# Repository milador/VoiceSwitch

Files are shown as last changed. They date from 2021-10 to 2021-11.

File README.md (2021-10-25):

# VoiceSwitch
An accessible voice activated switch using a HUZZAH32 – ESP32 Feather Board and an Amazon Echo

A HUZZAH32 board connected to a wheelchair using a 3.5mm audio jack (https://www.youtube.com/watch?v=OCM7eB8Ey9I)

# Setup Instructions

  Please Refer to the [Assembly Guide](https://github.com/milador/VoiceSwitch/blob/master/VoiceSwitch_Assembly_Guide.pdf).

# License 

## MIT License

Copyright (c) 2018 Milador

Permission is hereby granted, free of charge, to any person obtaining a copy of this software and associated documentation files (the "Software"), to deal in the Software without restriction, including without limitation the rights to use, copy, modify, merge, publish, distribute, sublicense, and/or sell copies of the Software, and to permit persons to whom the Software is furnished to do so, subject to the following conditions:

The above copyright notice and this permission notice shall be included in all copies or substantial portions of the Software.

THE SOFTWARE IS PROVIDED "AS IS", WITHOUT WARRANTY OF ANY KIND, EXPRESS OR IMPLIED, INCLUDING BUT NOT LIMITED TO THE WARRANTIES OF MERCHANTABILITY, FITNESS FOR A PARTICULAR PURPOSE AND NONINFRINGEMENT. IN NO EVENT SHALL THE AUTHORS OR COPYRIGHT HOLDERS BE LIABLE FOR ANY CLAIM, DAMAGES OR OTHER LIABILITY, WHETHER IN AN ACTION OF CONTRACT, TORT OR OTHERWISE, ARISING FROM, OUT OF OR IN CONNECTION WITH THE SOFTWARE OR THE USE OR OTHER DEALINGS IN THE SOFTWARE.

<p align="center">
MIT License
</p>

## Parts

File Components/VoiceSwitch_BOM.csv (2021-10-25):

Index | Quantity | Digikey Part Number | Manufacturer Part Number | Description | Unit Price (CAD) | Total Price (CAD) | Link
1 | 1 | 1528-2181-ND | 3405 | HUZZAH32 ESP32 FEATHER BOARD | 27.45 | 27.45 | https://www.digikey.ca/en/products/detail/adafruit-industries-llc/3405/7244967
2 | 1 | 1528-1658-ND | 2895 | ADAFRUIT NON-LATCHING MINI RELAY | 10.94 | 10.94 | https://www.digikey.ca/en/products/detail/adafruit-industries-llc/2895/5979891
3 | 1 | 1528-1560-ND | 2886 | FEATHER HEADER KIT FML | 1.31 | 1.31 | https://www.digikey.ca/product-detail/en/adafruit-industries-llc/2886/1528-1560-ND/
4 | 1 | 1528-1858-ND | 2750 | BATTERY LITHIUM 3.7V 350MAH (Optional) | 12.99 | 12.99 | https://elmwoodelectronics.ca/products/lithium-ion-polymer-battery-3-7v-350mah or https://www.digikey.com/en/products/detail/adafruit-industries-llc/2750/6612470
5 | 1 | SC1455-ND | 35PM1 | CONN JACK MONO 3.5MM PNL MNT | 4.38 | 4.38 | https://www.digikey.ca/en/products/detail/switchcraft-inc/35PM1/1288859
6 | 1 | 81044/12-24-6-DS-ND | 81044/12-24-6 | 81044/12-24-6 FEET HOOK-UP WIRE | 0.98 | 0.98 | https://www.digikey.ca/en/products/detail/te-connectivity-aerospace,-defense-and-marine/81044%2F12-24-6/6071077
7 | 2 | 36-4687-ND | 4687 | HEX NUT 0.197" NYLON M2.5 | 0.23 | 0.46 | https://www.digikey.ca/en/products/detail/keystone-electronics/4687/4499296
8 | 2 | 36-29334-ND | 29334 | MACH SCREW PAN SLOTTED M2.5X0.45 | 0.34 | 0.68 | https://www.digikey.ca/en/products/detail/keystone-electronics/29334/1532988
9 | 1 |  | Echo Dot | ECHO DOT OR OTHER ALEXA ENABLED DEVICE | 55 | 54.99 | https://www.amazon.ca/Echo-Dot-3rd-gen-Charcoal/dp/B07PDHT5XP/
 |  |  |  |  | Total | 114.18

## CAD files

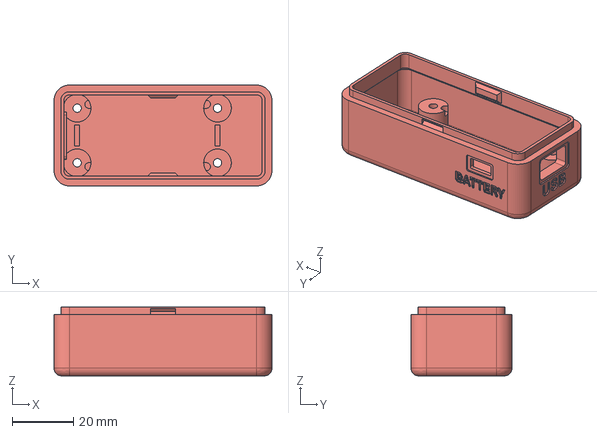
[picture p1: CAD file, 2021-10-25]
Hardware/Enclosure/STEP/VoiceSwitch_Bottom.step
71.0 x 32.9 x 22.4 mm

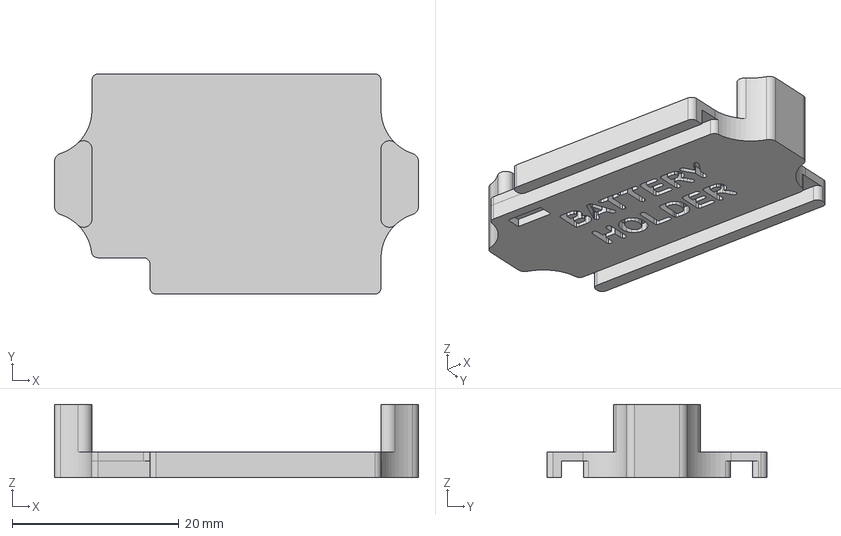
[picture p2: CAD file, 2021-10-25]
Hardware/Enclosure/STEP/VoiceSwitch_Battery_Holder.step
43.7 x 26.5 x 8.80 mm

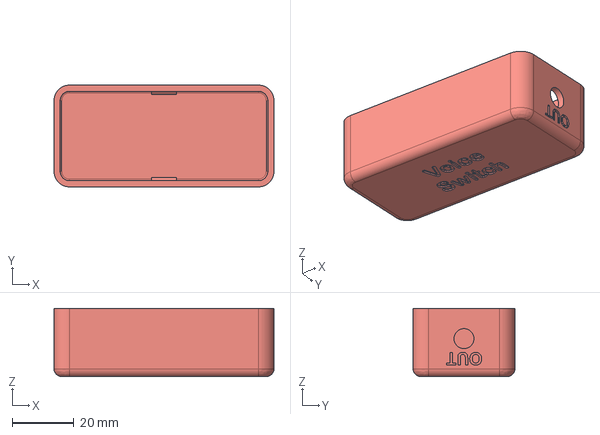
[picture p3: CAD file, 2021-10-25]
Hardware/Enclosure/STEP/VoiceSwitch_Top.step
71.0 x 32.9 x 22.0 mm

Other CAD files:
Hardware/Enclosure/STL/VoiceSwitch_Battery_Holder.stl
Hardware/Enclosure/STL/VoiceSwitch_Bottom.stl
Hardware/Enclosure/STL/VoiceSwitch_Top.stl

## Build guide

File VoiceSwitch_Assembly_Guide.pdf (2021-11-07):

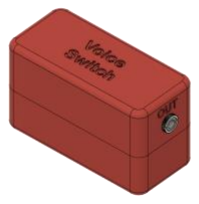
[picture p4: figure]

# VOICE SWITCH

Version 1.1

An accessible voice activated switch using a HUZZAH32 – ESP32 Feather Board and an Amazon Echo.

### Milador

1

## Table of Contents

Components | 2
Hardware Setup | 3
Enclosure design | 3
Assembly | 4
Software Setup | 20

2

Github Repository: https://github.com/milador/VoiceSwitch

### Components

1. HUZZAH32 – ESP32 Feather Board (1 x)
2. ADAFRUIT NON-LATCHING MINI RELAY (1 x)
3. FEATHER HEADER KIT FML (1 x)
4. (OPTIONAL) BATTERY LITHIUM 3.7V 350MAH (1 x)
5. CONN JACK MONO 3.5MM PNL MNT (1 x)
6. HOOK-UP WIRE (1 x)
7. HEX NUT 0.197" NYLON M2.5 (2 x)
8. MACH SCREW PAN SLOTTED M2.5X0.45 (2 x)
9. (OPTIONAL) ECHO DOT OR OTHER ALEXA ENABLED DEVICE (1 x)

3

### Hardware Setup

Enclosure design
The enclosure/housing files in STL format can be downloaded from GitHub repository under Hardware directory.

https://github.com/milador/VoiceSwitch/tree/master/Hardware/Enclosure

Please print the following STL files:

- 1 x VoiceSwitch_Top_Top.stl
- 1 x VoiceSwitch_Bottom.stl
- 1 x VoiceSwitch_Battery_Holder.stl (Optional)

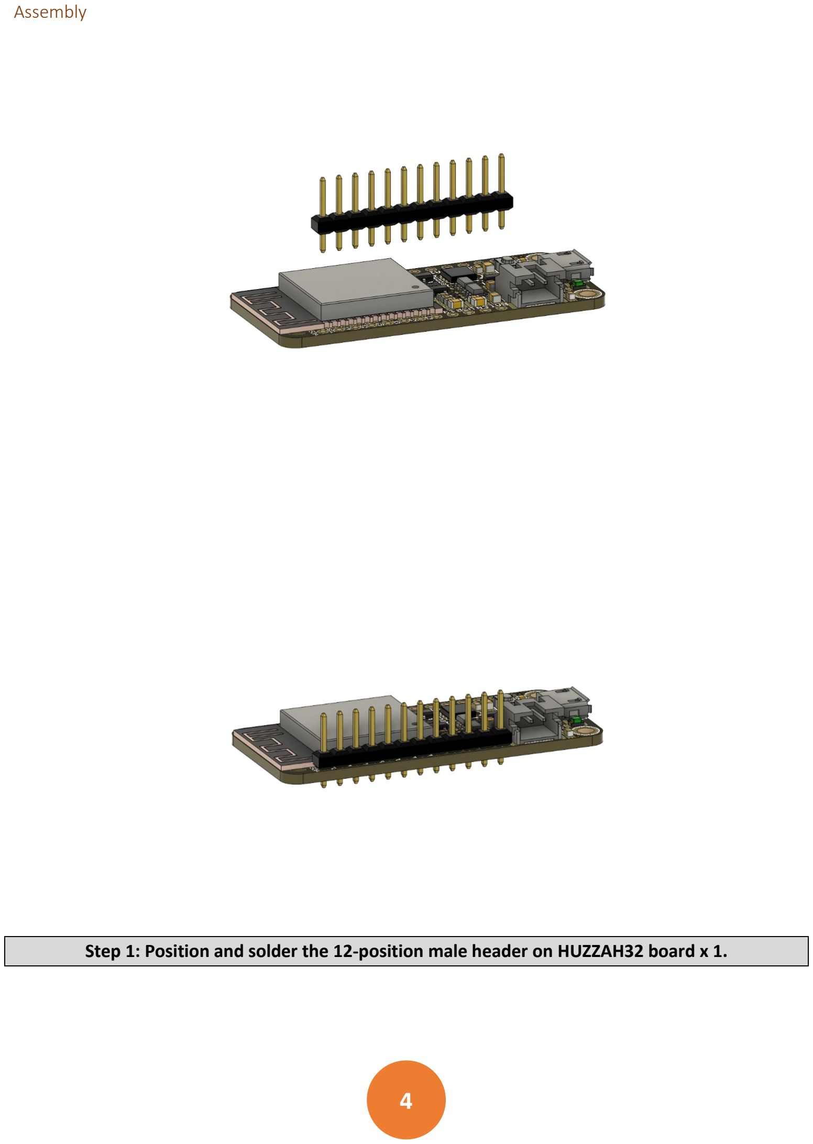
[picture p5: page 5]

4

Assembly

Step 1: Position and solder the 12-position male header on HUZZAH32 board x 1.

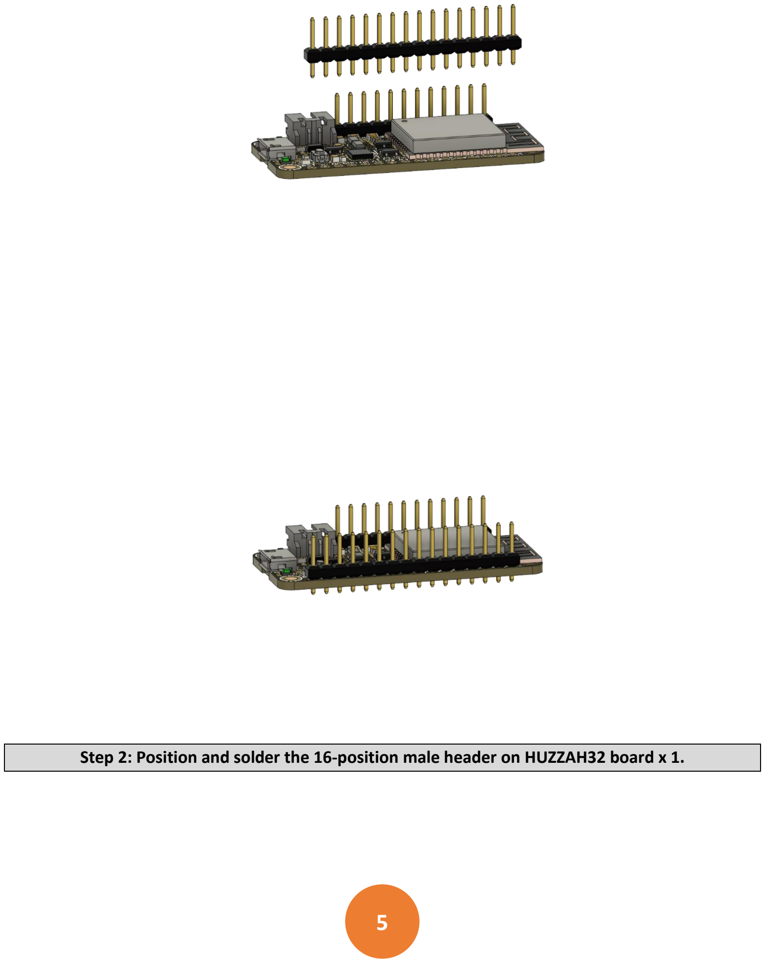
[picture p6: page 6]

5

Step 2: Position and solder the 16-position male header on HUZZAH32 board x 1.

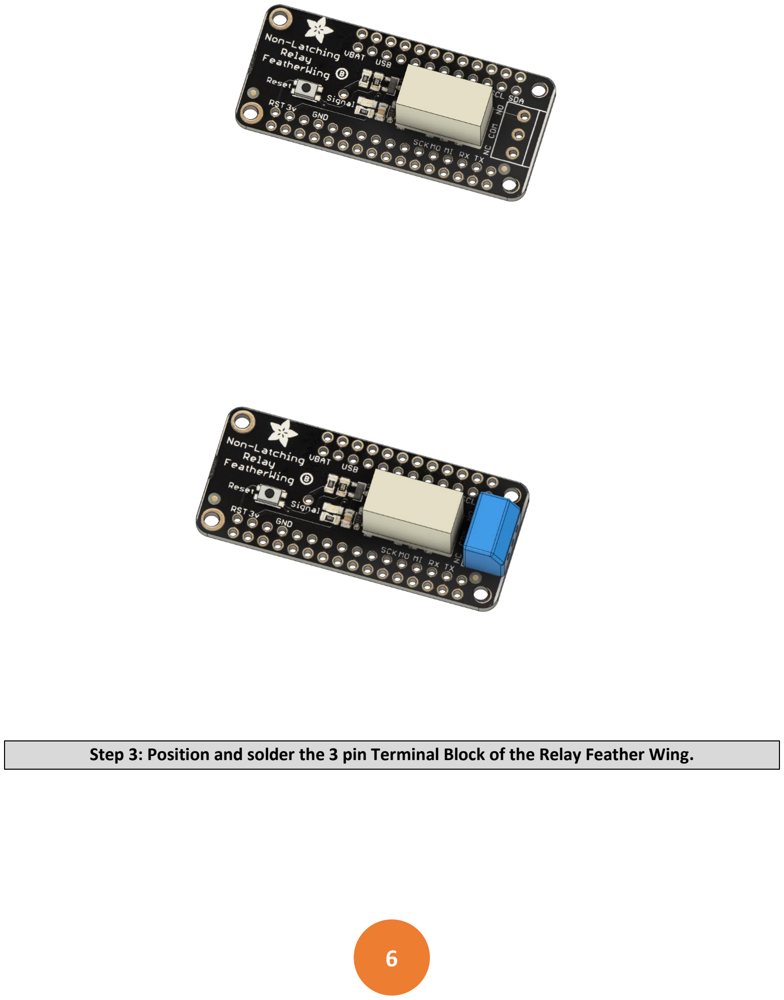
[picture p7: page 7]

6

Step 3: Position and solder the 3 pin Terminal Block of the Relay Feather Wing.

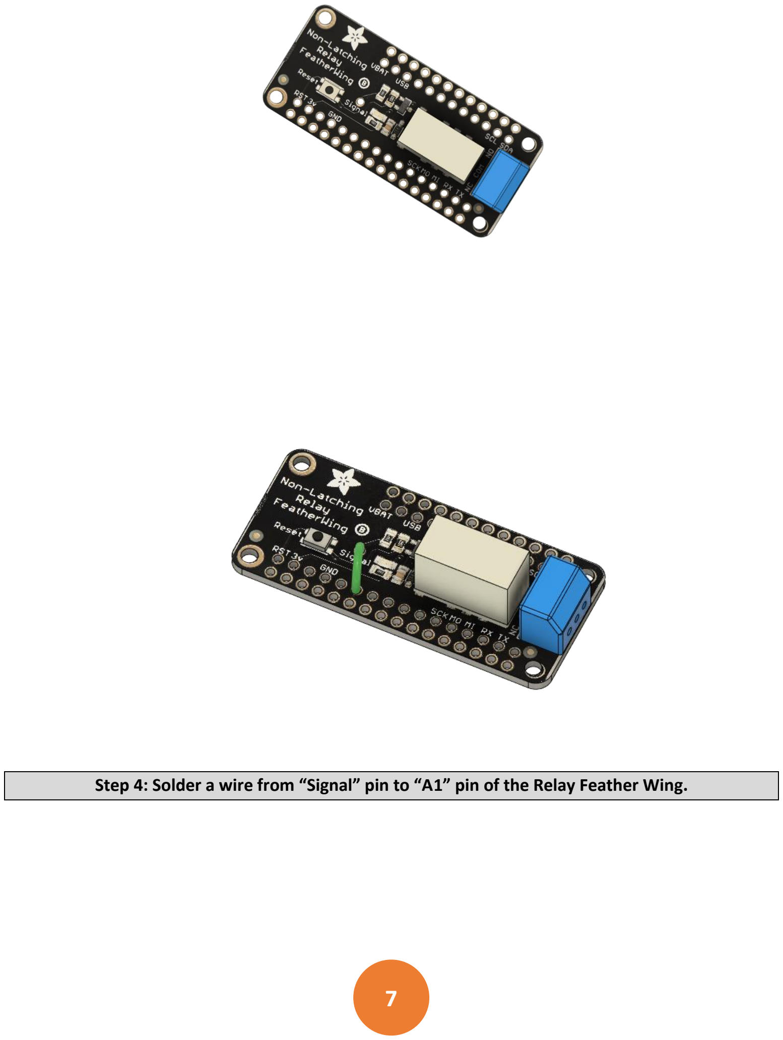
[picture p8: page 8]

7

Step 4: Solder a wire from “Signal” pin to “A1” pin of the Relay Feather Wing.

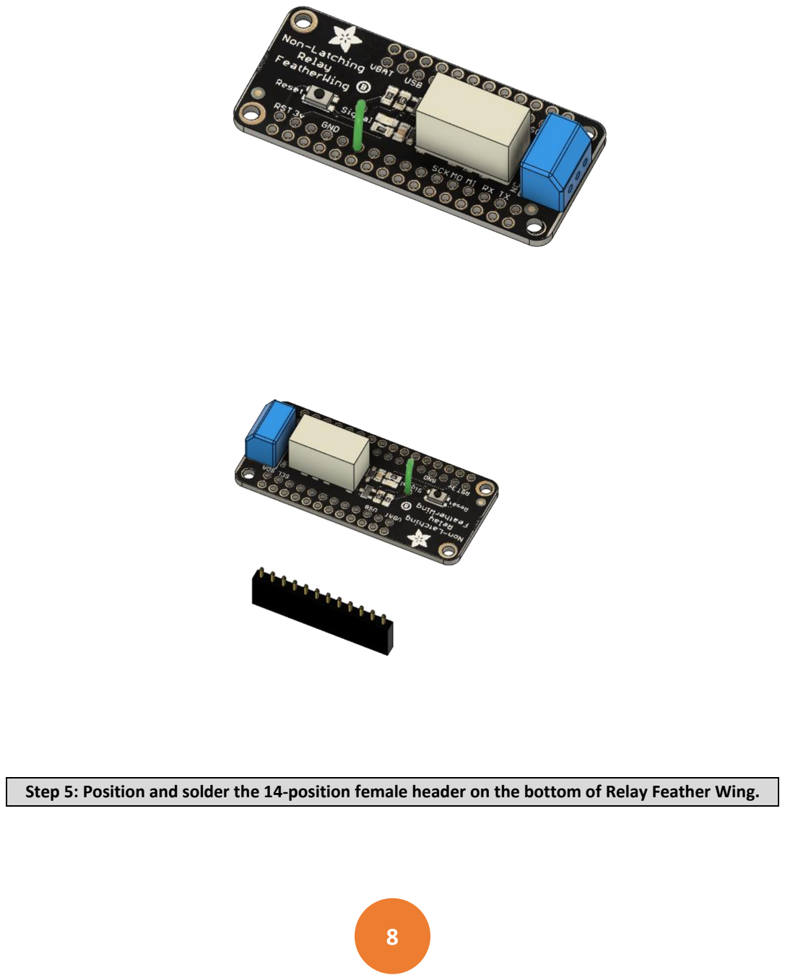
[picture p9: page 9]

8

Step 5: Position and solder the 14-position female header on the bottom of Relay Feather Wing.

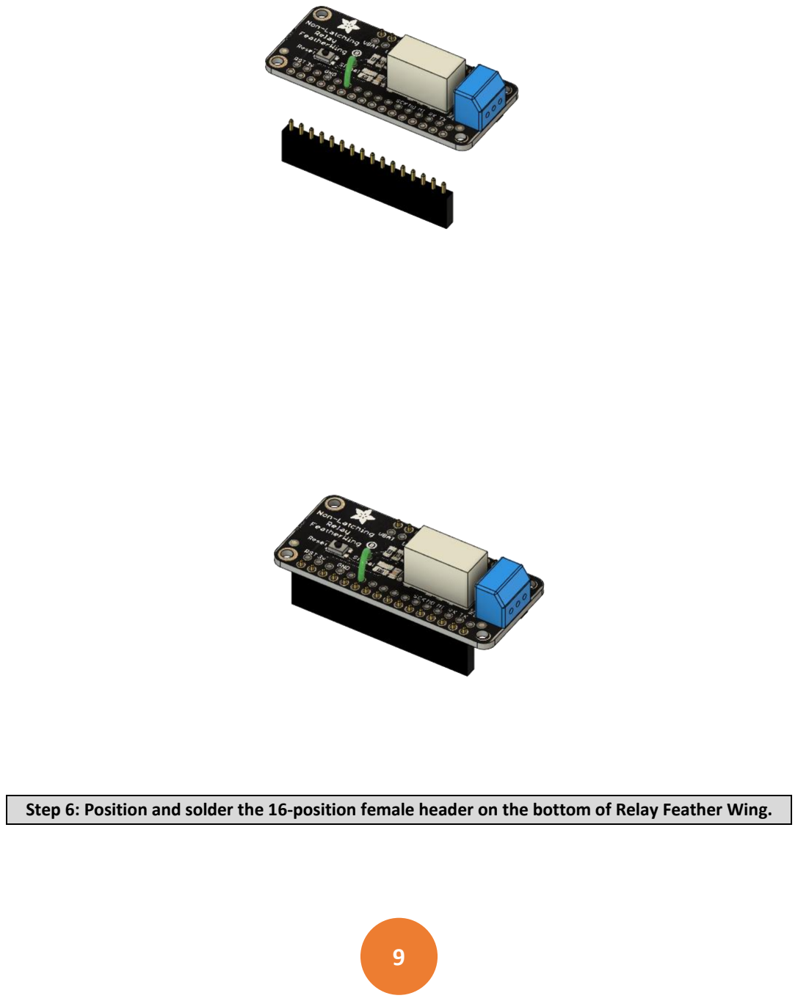
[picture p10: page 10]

9

Step 6: Position and solder the 16-position female header on the bottom of Relay Feather Wing.

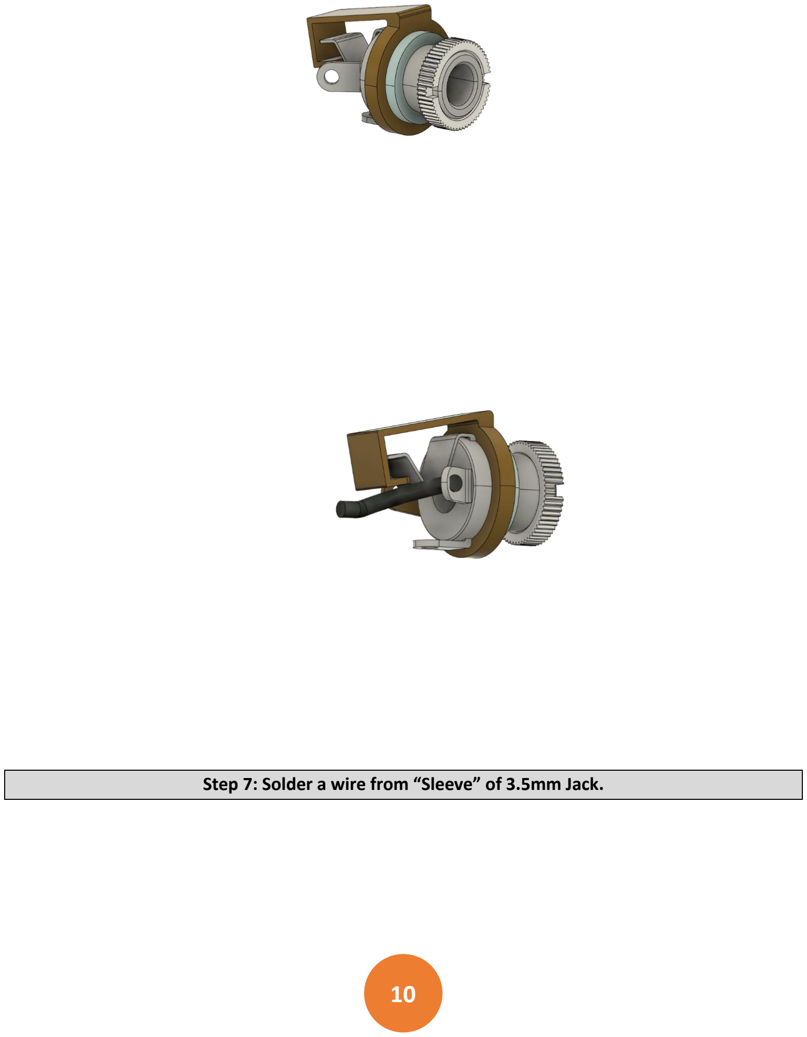
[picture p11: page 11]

10

Step 7: Solder a wire from “Sleeve” of 3.5mm Jack.

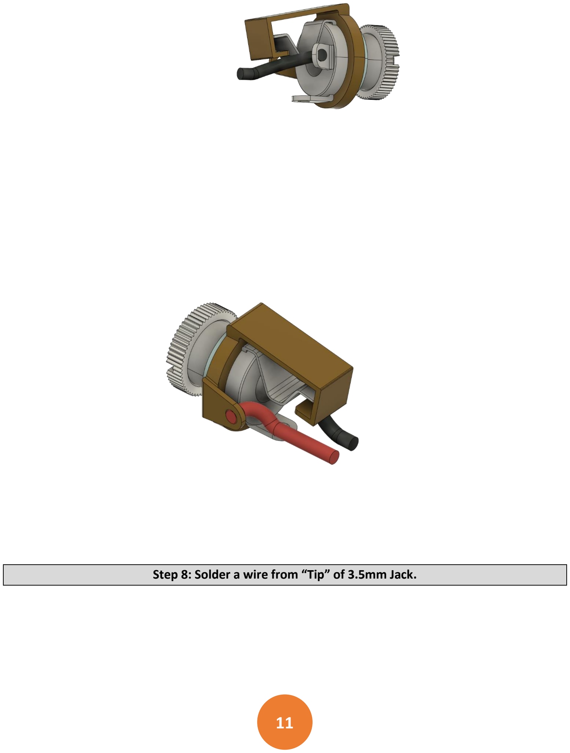
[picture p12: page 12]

11

Step 8: Solder a wire from “Tip” of 3.5mm Jack.

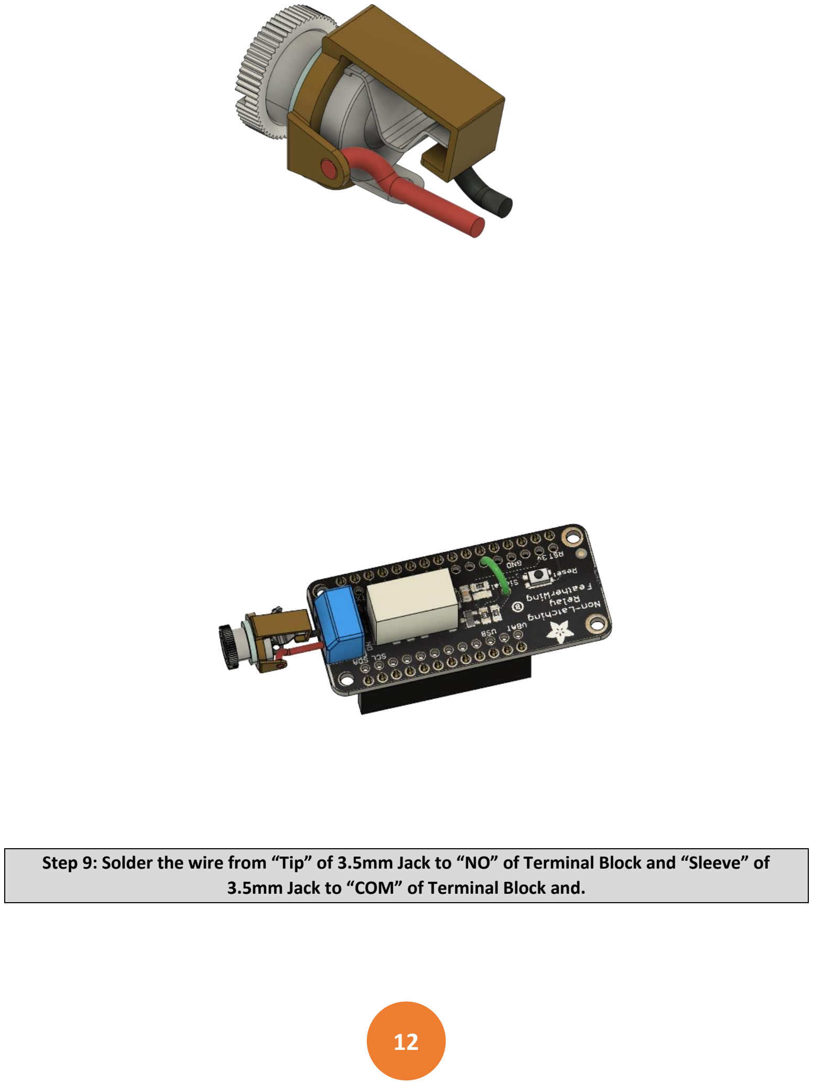
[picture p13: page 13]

12

Step 9: Solder the wire from “Tip” of 3.5mm Jack to “NO” of Terminal Block and “Sleeve” of 3.5mm Jack to “COM” of Terminal Block and.

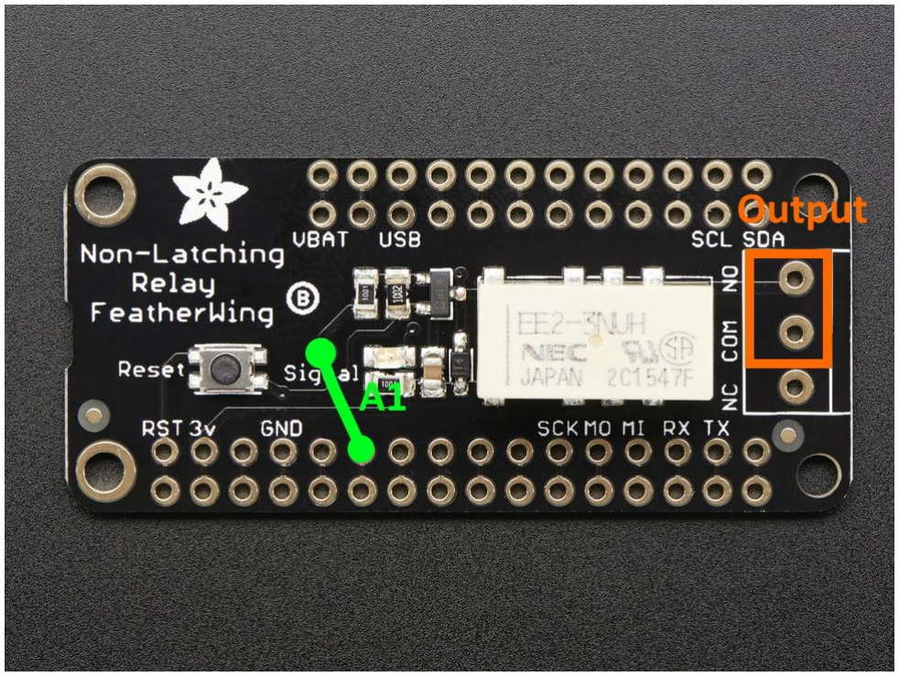
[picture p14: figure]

13

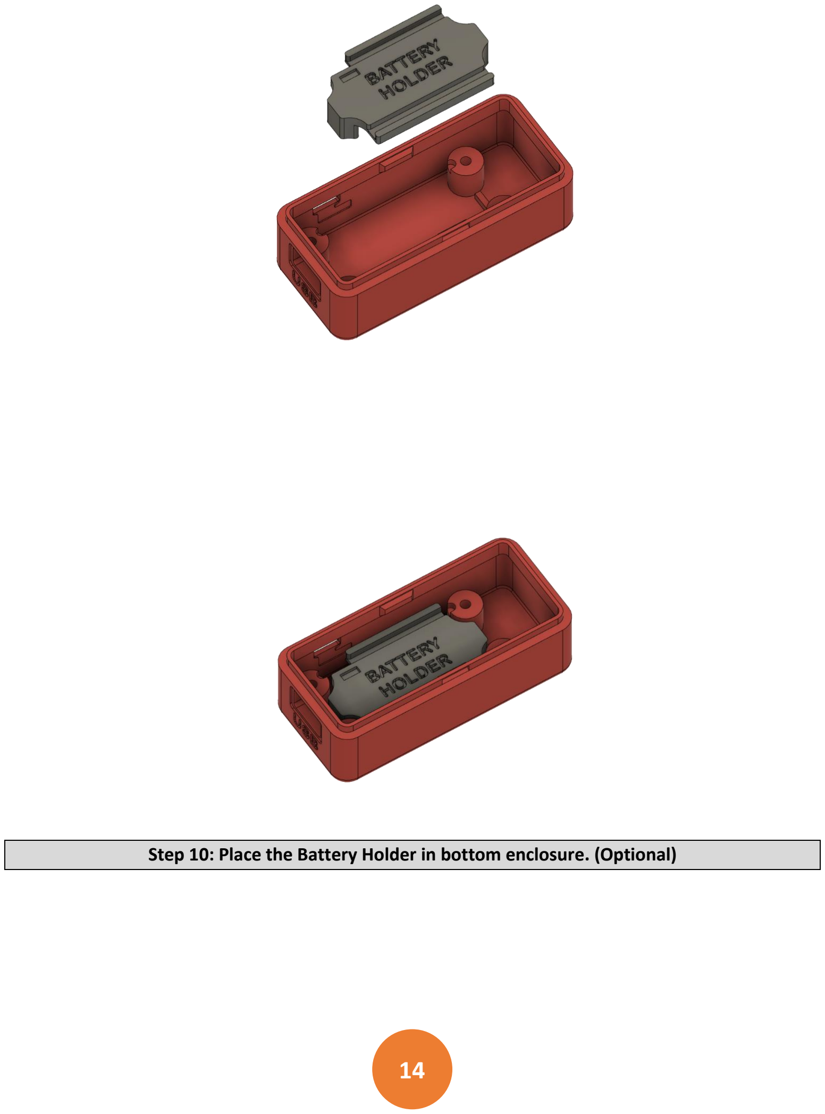
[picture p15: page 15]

14

Step 10: Place the Battery Holder in bottom enclosure. (Optional)

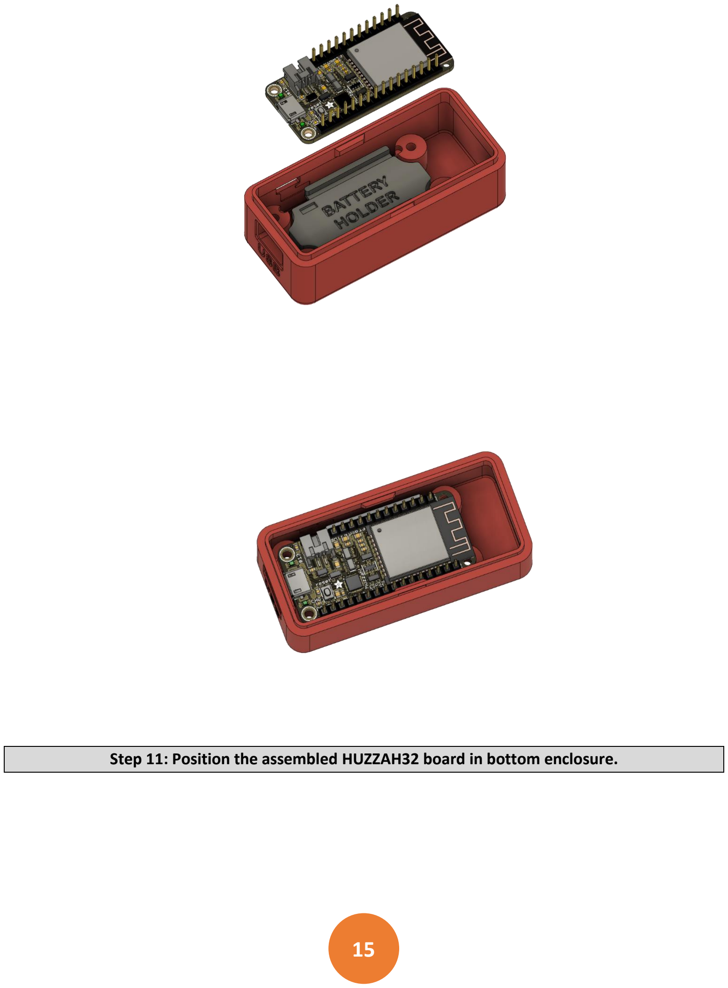
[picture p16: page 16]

15

Step 11: Position the assembled HUZZAH32 board in bottom enclosure.

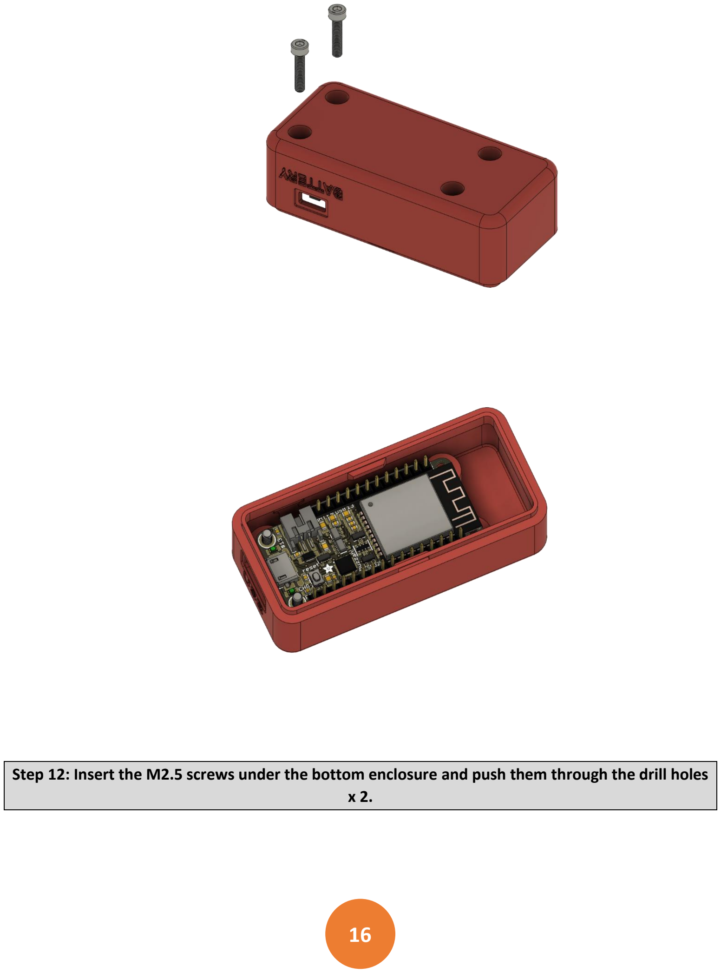
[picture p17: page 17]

16

Step 12: Insert the M2.5 screws under the bottom enclosure and push them through the drill holes x 2.

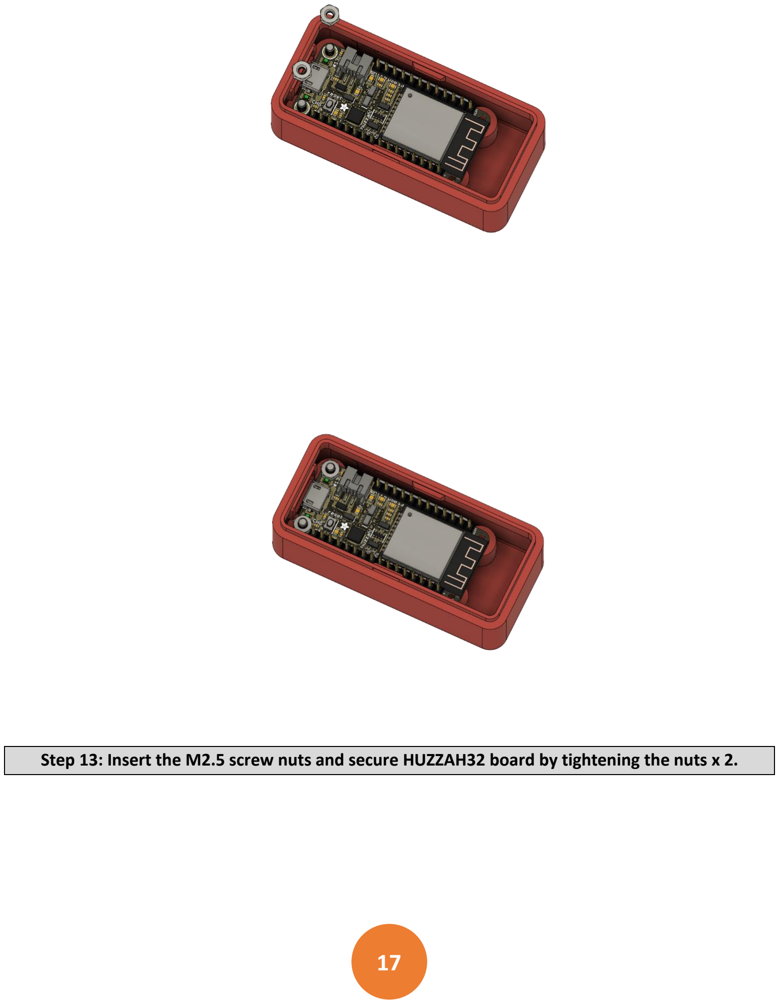
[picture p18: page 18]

17

Step 13: Insert the M2.5 screw nuts and secure HUZZAH32 board by tightening the nuts x 2.

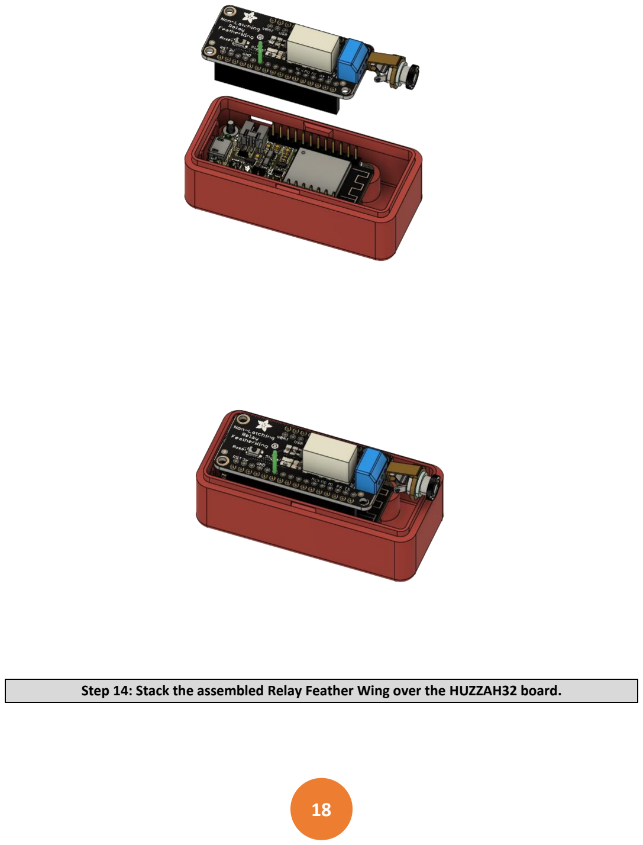
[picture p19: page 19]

18

Step 14: Stack the assembled Relay Feather Wing over the HUZZAH32 board.

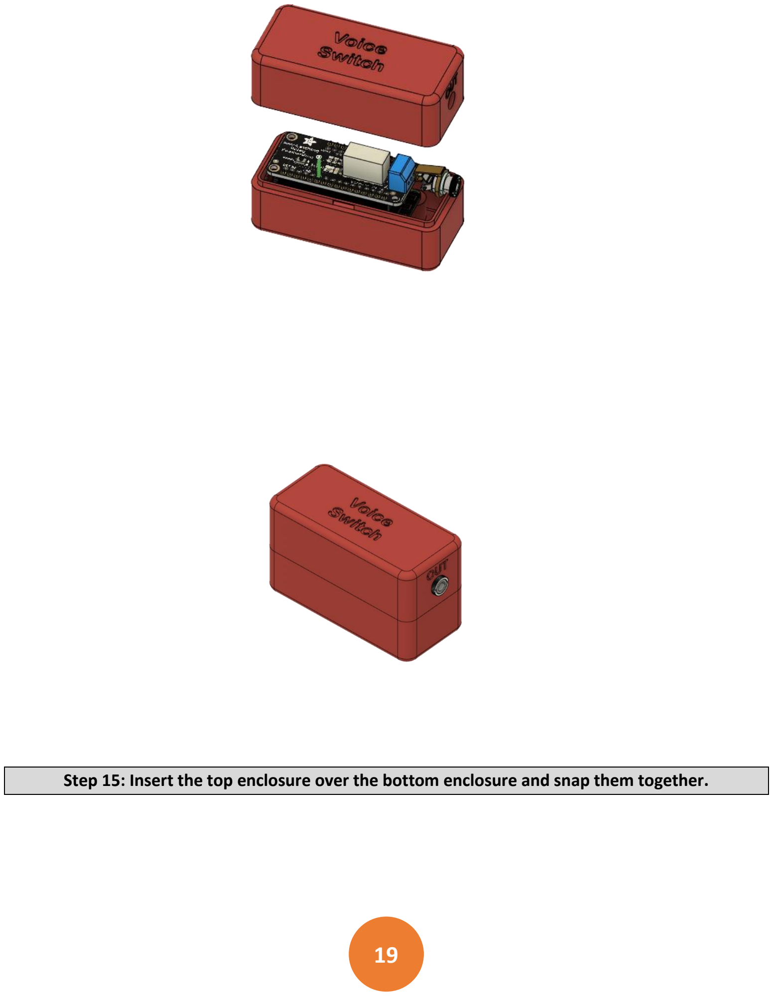
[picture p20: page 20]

19

Step 15: Insert the top enclosure over the bottom enclosure and snap them together.

20

### Software Setup

1. Setup an Adafruit IO (https://io.adafruit.com/) account according to the following instructions:
1.1. Create an Adafruit IO account
1.2. Create an AIO KEY
1.3. Copy your Adafruit IO key for later use in the code
1.4. Create an Adafruit IO feed with name of your switch. I used feed name Monkey as an example.
2. Setup your HUZZAH32 – ESP32 Feather Board
2.1. Download ESP32 library for Arduino IDE and install it according to the following instruction:

https://learn.adafruit.com/adafruit-huzzah32-esp32-feather/using-with-arduino-ide

2.2. Download Adafruit IO Arduino library and add it to libraries directory under Arduino installation

path in your computer.

https://github.com/adafruit/Adafruit_IO_Arduino

2.3. Download Adafruit Arduino library for MQTT support and add it to libraries directory under Arduino

installation path in your computer.

https://github.com/adafruit/Adafruit_MQTT_Library

2.4. Download Adafruit Arduino HTTP Client library and add it to libraries directory under Arduino

installation path in your computer.

https://github.com/arduino-libraries/ArduinoHttpClient

3. Setup your Alexa compatible device or Alexa application (Android (https://play.google.com/store/apps/details?id=com.amazon.dee.app) and iOS) (https://apps.apple.com/us/app/amazon-alexa/id944011620) on your smartphone.
4. Setup IFTTT account 3.1. Create an IFTTT account at https://ifttt.com.
5. Create Momentary switch recipe
5.1. Open Ifttt application on your smartphone.
5.2. Click on the Create button to create a recipe.
5.3. Click on If This Add button to add the trigger block.
5.4. Search and select Amazon Alexa as trigger service.
5.5. Click on Say a specific phrase block to select the trigger phrase.
5.6. Enter the method phrase to activate the switch. I used phrase Monkey switch as an example.
5.7. Click on Then That Add button to add the action service block.
5.8. Search and select Adafruit as action service.
5.9. Select Send data to Adafruit IO block.
5.10. Enter Monkey feed as the Feed Name.
5.11. Enter switch as the Data to save.

21

5.12. Click on the Continue button.
5.13. Click on the Continue button again.
5.14. Review the applet logic and click on the Finish button.
6. Create Switch on recipe
6.1. Open Ifttt application on your smartphone.
6.2. Click on the Create button to create a recipe.
6.3. Click on If This Add button to add the trigger block.
6.4. Search and select Amazon Alexa as trigger service.
6.5. Click on Say a specific phrase block to select the trigger phrase.
6.6. Enter the method phrase to activate the switch. I used phrase Monkey on as an example.
6.7. Click on Then That Add button to add the action service block.
6.8. Search and select Adafruit as action service.
6.9. Select Send data to Adafruit IO block.
6.10. Enter Monkey feed as the Feed Name.
6.11. Enter switch as the Data to save.
6.12. Click on the Continue button.
6.13. Click on the Continue button again.
6.14. Review the applet logic and click on the Finish button.
7. Create Switch off recipe
7.1. Open Ifttt application on your smartphone.
7.2. Click on the Create button to create a recipe.
7.3. Click on If This Add button to add the trigger block.
7.4. Search and select Amazon Alexa as trigger service.
7.5. Click on Say a specific phrase block to select the trigger phrase.
7.6. Enter the method phrase to activate the switch. I used phrase Monkey off as an example.
7.7. Click on Then That Add button to add the action service block.
7.8. Search and select Adafruit as action service.
7.9. Select Send data to Adafruit IO block.
7.10. Enter Monkey feed as the Feed Name.
7.11. Enter switch as the Data to save.
7.12. Click on the Continue button.
7.13. Click on the Continue button again.
7.14. Review the applet logic and click on the Finish button.

22

8. Setup the VoiceSwitch.ino code
8.1. Open VoiceSwitch.ino file using Arduino IDE.
8.2. Make a copy of your IO_USERNAME and IO_KEY from Adafruit IO account and paste them in the

config.h file.

8.3. Replace your_ssid with your WiFi's SSID and your_pass with your WiFi's password in the config.h

file.

8.4. Verify and upload VoiceSwitch.ino code to your HUZZAH32 – ESP32 Feather Board.
9. Make sure the feed data status and status of your device match. You can manually set it to on/off to

match it.
